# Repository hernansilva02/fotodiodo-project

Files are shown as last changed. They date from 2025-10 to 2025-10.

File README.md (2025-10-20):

# Fotodiodo Project — Detector con fotodiodo + TIA

Proyecto académico/open-hardware para el diseño, simulación y fabricación de un detector basado en **fotodiodo PIN** con **amplificador transimpedancia (TIA)**. El repositorio incluye esquemáticos y PCB en KiCad, modelos/SPICE para simulación, gerbers listos para fabricación y documentación en LaTeX.

> Licencia: **CERN Open Hardware License v1.2** (incluida en el repo).

---

## ✨ Características

- **Hardware KiCad**: esquemáticos y PCB en `KiCAD/` con vistas 2D/3D y archivos de fabricación en `gerbers/`.
- **Simulación**: netlists y archivos en `spice/` para análisis de ruido, frecuencia y transitorios del TIA.
- **Documentación**: fuentes LaTeX en `docs/` (compilables con `latexmk` o `pdflatex + bibtex`).
- **Datasheets** de componentes relevantes en `datasheets/`.
- **Licencia**: archivo `CERN_OPEN_HARDWARE_LICENSE_OHL_v_1_2.txt` en la raíz.

---

## 🔧 Requisitos

- **KiCad** (>= 6.x recomendado) para abrir `KiCAD/`.
- **Simulador SPICE** (LTspice/Ngspice) para `spice/`.
- **LaTeX** para compilar `docs/` (p. ej. `latexmk` o `pdflatex + bibtex`).

---

## ▶️ Cómo usar

### 1) Hardware (KiCad)
1. Abrí el proyecto desde `KiCAD/`.
2. Revisá el esquemático y el stackup; validá DRC/ERC.
3. Para visualizar en 3D, usá el visor de KiCad.
4. Si necesitás fabricar, exportá desde el proyecto o usá los **archivos listos** en `gerbers/`.

### 2) Simulación (SPICE)
1. Abrí los archivos de `spice/` con tu simulador.
2. Corré análisis **AC** (ganancia/banda), **TRAN** (respuesta a pulsos) y **ruido**.
3. Ajustá la **Rf** del TIA y **Cf** de compensación según tu fotodiodo/carga esperada.

### 3) Documentación (LaTeX)
- Compilación rápida:
  ```bash
  cd docs
  latexmk -pdf
  # o, alternativamente
  pdflatex main.tex && bibtex main && pdflatex main.tex && pdflatex main.tex

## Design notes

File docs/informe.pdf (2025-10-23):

# Detector de Part´ıculas Beta

Hernan Alejandro Silva ´
Facultad Regional Avellaneda Universidad Tecnologica Nacional ´ Buenos Aires, Argentina
hernansilva2002@gmail.com

El´ıas Ram´ırez
Facultad Regional Avellaneda Universidad Tecnologica Nacional ´ Buenos Aires, Argentina
ramirezelias.marcos@gmail.com

Florencia Mincone
Facultad Regional Avellaneda Universidad Tecnologica Nacional ´ Buenos Aires, Argentina
flormincone1@gmail.com

Nicolas Lahorca ´
Facultad Regional Avellaneda Universidad Tecnologica Nacional ´ Buenos Aires, Argentina
nicolas.lahorca.k@gmail.com

Luciano Justiniano
Facultad Regional Avellaneda Universidad Tecnologica Nacional ´ Buenos Aires, Argentina
luciano.nicolas.justiniano@gmail.com

Abstract—Constantemente los objetos que nos rodean emiten part´ıculas que los sentidos humanos no son capaces de percibir. Estas part´ıculas pueden ser perjudiciales para la salud y es necesario cuantificarlas y/o detectarlas para evitar o reducir la exposicion a ellas. Para lograr ese objetivo, en este documento se ´
presenta la realizacion de un dispositivo que cumpla la funci ´ | on de ´
detectar un tipo de radiacion, llamada radiaci ´ | on´ β. En particular,
se hara hincapi ´ | e en la radiaci ´ | on por emisi ´ | on de electrones, a este ´
tipo de radiacion se la conoce como radiaci ´ | on´ | β−. Ademas, ´
se propone el analisis de su principio de funcionamiento, los ´ materiales necesarios para su construccion y sus limitaciones. ´
I. INTRODUCCION´
El presente documento sirve como informe sobre el proyecto
de fin de ano de la asignatura F ˜ | | | ´ısica Electronica. Dicho ´
proyecto se trata de un detector y contador de part´ıculas beta, cubriendo de esta forma el tema radiacion de la asignatura. ´
Para mas informaci ´ | on sobre el proyecto, se recomienda visitar ´
el repositorio del mismo [1].

II. PRINCIPIO DE FUNCIONAMIENTO
A. ¿Que son las radiaciones β?
Las radiaciones β son un tipo de radiacion ionizante, la cual ´ se caracteriza por emitirse durante el proceso de desintegracion´ o decaimento β. Dicho proceso puede producirse de dos diferentes formas.
1) Emision de electrones ´ | : Un nucleo inestable de un ´ | atomo ´
emite un electron y un antineutrino, conviritiendo de esta ´
manera un neutron en un prot ´ | on como ´ | Desintegracion´
β−.
2) Emision de positrones ´ | : El nucleo inestable emite un ´
positron, es decir, la antipart ´ | | | ´ıcula del electron, junto ´
con un neutrino. De esta forma se logra transformar un
proton en un neutr ´ | on. Este proceso recibe el nombre de ´
Desintegracion´ β+.
Generalmente, las fuentes mas comunes de radiaci ´ | on de ´
part´ıculas β son piedras con pequenas cantidades de uranio, ˜ y diferentes fuentes de potasio, como el cloruro de potasio
(KCl), el cual contiene baja cantidad del is ´ | otopo potasio 40 ´
(K40), capaz de emitir part ´ | | ´ıculas β−.
B. Formas de captar las part´ıculas
El dispositivo electronico m ´ | as estudiado y utilizado para ´
detectar la radiacion de diferentes tipos de part ´ | ´ıculas es el
diodo PIN o fotodiodo. Como muestra la Fig. 1, este es similar en cuanto a estructura a un diodo de juntura PN, la diferencia radica en que el PIN tiene una zona de material semiconductor intr´ınseco (zona I) entre la zona dopada positivamente (zona
P) y la zona dopada negativamente (zona N).
Al ser un material semiconductor, la zona I contiene atomos ´ de silicio que, al momento de ser impactados por una part´ıcula irradiada debido a una fuente radioactiva, genera la rotura de
los enlaces covalentes del atomo, produciendo un ´ | par electron- ´
laguna. La generacion de este par tiene como consecuencia un ´ pulso de corriente de decenas hasta cientos de microampere que atraviesan al diodo. Esta corriente puede ser medida. Cuando al diodo se lo polariza en forma inversa (catodo con ´
potencial mas alto que el del ´ | anodo), se generan dos regiones ´
de vaciamiento: La primera se encuentra localizada entre la zona P y la zona I, y la otra entre dicha zona intr´ınseca y la zona N; en estas regiones, no se encuentran portadores libres, sino que exisen iones fijos cargados positiva y negativamente. Estos iones fijos son los responsables que en dichas regiones
se encuentre un campo electrico, el c ´ | ual atrapa e impulsa a los ´
portadores, aumentando la intensidad de corriente electrica a ´ traves del diodo. ´
Anodo (A) ´ | Catodo (K) ´

P

+ | I | N +

Wi

Fig. 1. Corte transversal de una estructura t´ıpica del diodo PIN

C. El fotodiodo como detector de part´ıculas β

La zona intr´ınseca explicada anteriormente es conocida como zona sensible, porque es donde las part´ıculas irradiadas impactan. Como se menciona en [2], las zonas sensibles de los fotodiodos son capaces de absorber algunos tipos de radia-
ciones ionizantes. La deteccion de las part ´ | ´ıculas que impactan
esta directamente relacionada con la profundidad de la zona ´ sensible del diodo; esta zona (region de vaciamiento) aumenta ´ de profundidad al elevar el voltaje de polarizacion inversa del ´
dispositivo, dicha relacion responde matem ´ | aticamente a ´

d(V ) = εrε0A
C(V )
| (1)

donde:
- d(V) es la profunidad de la zona sensible.
- εr es la permitividad relativa del material, en este caso el Si (silicio).
- ε0 es la permitividad del vac´ıo.
- A es el area f ´ ´ısica de la zona sensible del diodo.
- C(V) es la capacitancia del diodo a un determinado nivel de voltaje de polarizacion inversa. ´
Este valor de profundidad permite conocer la energ´ıa
cinetica m ´ | axima que se puede detectar de una part ´ | ´ıcula. Como
se menciono anteriormente, los valores de inter ´ | es correspon- ´
den a part´ıculas β− (electrones). Para establecer el valor de energ´ıa mencionado, es necesario conocer la magnitud del rango CSDA (continuos slowing down approximation). El rango CSDA es una aproximacion muy cercana de la media de ´ longitud de una trayectoria que recorre una part´ıcula cargada a medida que se frena hasta alcanzar el reposo [3]. Para los electrones, los valores del CSDA estan tabulados en [3]. ´ Para obtener una medicion fiable, es necesario que el rango ´ CSDA sea menor o igual que la profundidad de la zona sensible del diodo; esto es
Rp ≤ d(V ) | (2)

donde Rp es el rango CSDA.
De esta forma, la energ´ıa de la part´ıcula incidente es completamente disipada en el interior de la zona sensible.

III. CARACTER´ISTICAS CONTRUCTIVAS DEL DETECTOR

El dispositivo a realizar para detectar las part´ıculas tiene
como foco ser portable y producir una senal de detecci ˜ | on a la ´
salida con amplitud observable al medir con un osciloscopio digital. Con estos objetivos definidos, el dispositivo estara´ compuesto por dos etapas:
- Etapa de deteccion: La opci ´ | on mas documentada para la ´
deteccion de estas part ´ | ´ıculas es el diodo PIN BPW34, que
es posible observar en la Fig. 2(a); si se logra aislarlo completamente de la luz incidente y de interferencias electromagneticas, es capaz de detectar radiaciones ion- ´ izantes en su zona sensible.

Para aumentar la superficie total de deteccion, el circuito ´ utiliza 4 diodos en paralelo. Esto no modifica el valor de profundidad de la zona sensible calculada a partir de (1).
- Etapa de amplificacion: Es necesario tener un nivel de ´ ruido muy reducido, ya que un nivel alto esconder´ıa los picos debido a los impactos de las part´ıculas. El candidato ideal que satisface esos requerimientos es un amplificador operacional de alta impedancia de entrada, como lo es la serie OPAx134 del fabricante Texas Instruments. A su vez, esta etapa esta compuesta por una etapa de tran- ´ simpedancia (conversion de la corriente de los fotodiodos ´
en tension) y otra de amplificaci ´ | on diferencial. ´
Ambas etapas deben tener su especificacion correspondi- ´ ente.
A. Etapa de deteccion´

Debido a que uno de los objetivos es que el dispositivo detector sea portable, la alimentacion del circuito es de una ´ bater´ıa de 9 V, con una tension nominal de 9,9 V. Con ´ este valor de alimentacion, el circuito amplificador entrega ´ aproximadamente 8 V de polarizacion inversa a los diodos. ´ La Fig. 2(b) muestra que para un nivel de tension de 8 V de ´ VR corresponde una capacitancia de aproximadamente 22 pF. Reemplazando la capacitancia (para 8 V de VR) en (1), se obtiene

d(V ) = 11, 68 × 8, 85 × 10⁻¹² F · m⁻¹ × 7.02 mm² 22 pF
d(V ) = 32, 98 µm
d(V ) ≈ 33 µm
Esto nos indica que un electron puede viajar como m ´ | aximo ´
33 µm dentro de la zona sensible, de manera tal que se cumpla lo expresado con anterioridad en (2).
Debido a que la base de datos de [3] expresa los valores de rango CSDA en unidades de g/cm²
, es necesario que el d(V) calculado este tambi ´ en en dicha unidad; para esto, calculamos ´

σ = ρ t

donde σ es la densidad superficial, ρ es la densidad del silicio y t es el espesor de la zona sensible (d(V) calculado).
Para 33 µm, esto es

σ = ρ t
σ = 2, 32 g · cm⁻³ × 0, 0033 cm = 7, 6 × 10⁻³

g · cm⁻²

En la base de datos de [3] es posible observar que para el
Si, la energ´ıa cinetica m ´ | axima del electr ´ | on para un rango de ´
7, 6 × 10⁻³ g · cm⁻² | es 60 KeV.
Con el fin de anular interferencias electromagneticas exter- ´ nas y la luz del ambiente, el circuito se ubica dentro de un gabinete estanco de aluminio.

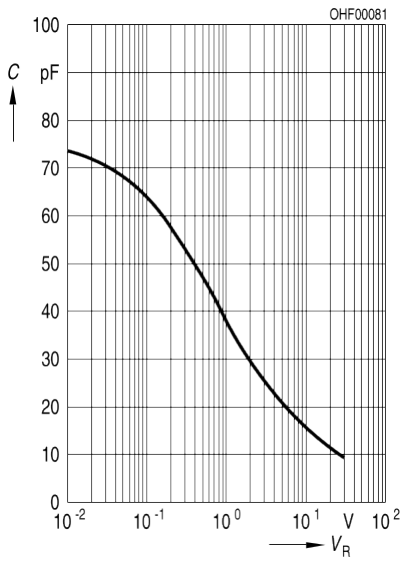
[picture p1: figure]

(a) (b)

Fig. 2. Fotodiodo BPW34S de la marca Osram. (a) Imagen real del fotodiodo. ´
(b) Curva caracter´ıstica C-V del BPW34S
B. Etapa de amplificacion´
El amplificador operacional, cuyas descripciones se explico´ anteriormente, consta de 2 etapas; ambas se pueden ver en la Fig. 3.
- Etapa de transimpedancia (primer etapa): Para transformar los picos de corriente en picos de voltaje es necesario utilizar un primer amplificador en configuracion´ transimpedancia; su caracter´ıstica fundamental es que la corriente generada en los diodos (decenas de microampere) atraviesa una resistencia de realimentacion de valor ´ grande, generando, por ley de Ohm, una caida de tension´ en ella. A la salida del primer amplificador tendremos

Vout1 = Vref1 − ID Rf b

donde Vref1 = V R1/(R1 + R2) es la tension de ´ referencia del primer amplificador; su valor tiene que ser 8 V y se logra a partir del divisor de voltaje entre las resistencias R1 y R2 de la Fig. 3. ID es la corriente de los diodos y Rfb es la resistencia de realimentacion´ (feedback), equivalente a R3 en la Fig. 3
- Etapa de amplificacion (segunda etapa): ´ | | | Vout1 es de valor
de tension muy d ´ | ebil, por ello es necesario amplificar la ´
salida de la primer etapa. Esto es posible mediante un segundo amplificador que toma como entrada Vout1. Al utilizar 2 amplificadores operacionales (uno por etapa), es necesario adoptar el amplificador OPA2134 de la l´ınea OPAx134 previamente mencionada.

IV. LIMITACIONES DEL DISENO˜

Las limitaciones o posibles mejoras del diseno actual son ˜ las siguientes
1) Niveles de energ´ıa cinetica detectables: Como se ha ´
expresado anteriormente, el nivel maximo de energ ´ | ´ıa
medible es 60 KeV, lo cual es un valor relativamente bajo ´
para part´ıculas β−; part´ıculas con mas energ ´ | ´ıa no seran´
medidas correctamente. Esto es debido principalmente al
area efectiva de detecci ´ | on ( ´ | area f ´ | ´ısica de la zona sensible
de los diodos) y al valor de capacitancia del diodo para

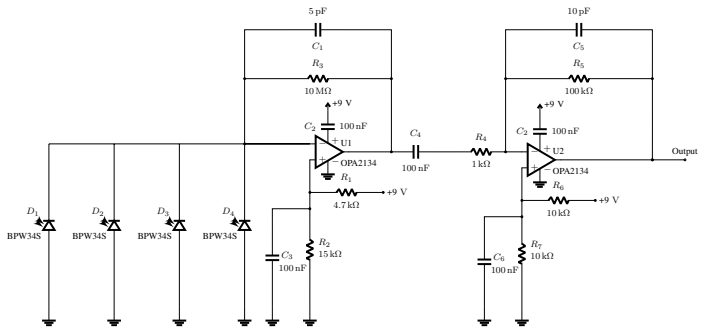
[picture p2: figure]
BPW34S; −OPA2134; OPA2134; Output

Fig. 3. Circuito completo

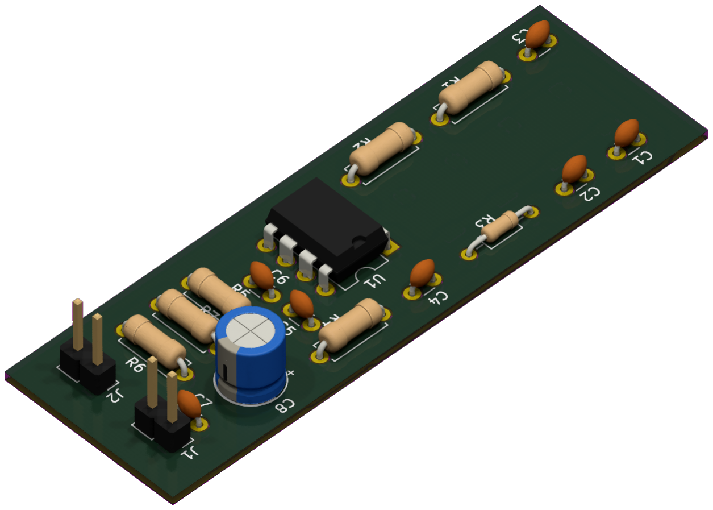
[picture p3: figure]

(a)

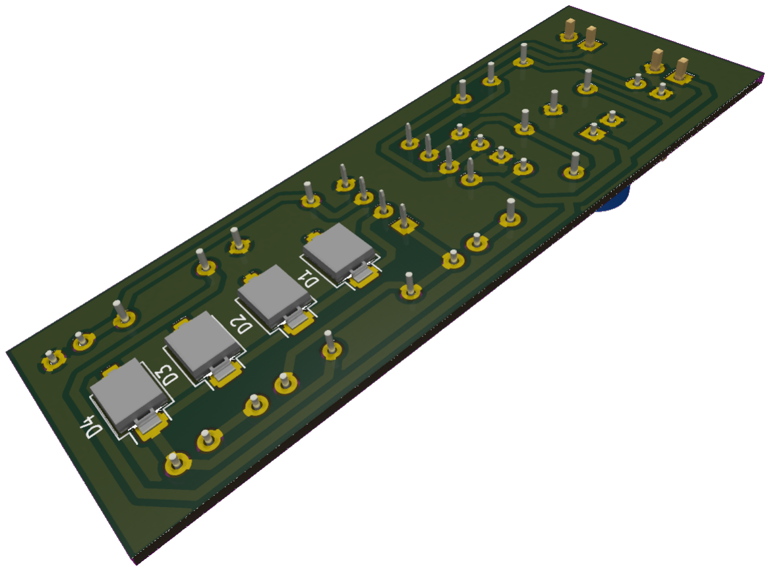
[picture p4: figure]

(b)

Fig. 4. Modelado 3D del PCB. (a) Parte frontal, (b) parte posterior

VR dado. Una mejora viable para este problema es el aumento del voltaje de alimentacion, de manera tal que ´ aumente VR.
2) Nivel de ruido: el capacitor C4 que se puede observar en la Fig. 3 tiene un papel fundamental en los niveles de ruido de la salida del circuito. Emp´ıricamente se pudo advertir que utilizando un valor de 22 pF en lugar de 5 pF, las mediciones de los picos fueron mas limpias. ´
V. CONCLUSIONES
Aunque el diseno de detectores de part ˜ | ´ıculas con fotodiodos
requiere de un nivel de precision muy grande para evitar ca- ´ pacitancias parasitas y obtener el menor nivel de ruido posible ´ montado en la senal de salida, es posible realizar mediciones ˜ de radiacion´ β− utilizando un amplificador operacional basado en JFET en configuracion transimpedancia. ´

REFERENCES

[1] H. Silva, “Detector de part´ıculas beta,” [Accedido: 23 Oct. 2025]. [Online]. Available: https://github.com/hernansilva02/fotodiodo-project. git
[2] O. Keller, M. Benoit, A. Muller, and S. Schmeling, “Smartphone and ¨ tablet-based sensing of environmental radioactivity: Mobile low-cost measurements for monitoring, citizen science, and educational purposes,” Sensors, vol. 19, 2019. [Online]. Available: https://www.mdpi.com/1424-8220/19/19/4264

[3] M. Berger, J. Coursey, M. Zucker, and J. Chang, “Stopping-
power | & | range | tables | for | electrons, | protons, | and | helium
ions,” National Institute of Standards and Technology, Tech. Rep., October 2009. [Online]. Available: https://www.nist.gov/pml/stopping-power-range-tables-electrons-protons-and-helium-ions
[4] U.S Department of Energy. Doe explains...beta decay. [Online]. Available: https://www.energy.gov/science/doe-explainsbeta-decay
[5] Ozel, “Diy particle detector,” [Accedido: 23 Oct. 2025]. [Online]. Available: https://github.com/ozel/DIY particle detector.git

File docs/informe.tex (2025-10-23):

\documentclass[a4paper,conference]{IEEEtran}
\usepackage{graphicx}
\usepackage{amsmath}
\usepackage{url}
\usepackage[RPvoltages]{circuitikz}
\usepackage{tikz}
\usepackage{siunitx}
\ifCLASSOPTIONcompsoc
    \usepackage[caption=false,font=normalsize,labelfont=sf,textfont=sf]{subfig}
\else
    \usepackage[caption=false,font=footnotesize]{subfig}
\fi

\makeatletter
\newcommand{\authornewline}{
        \end{@IEEEauthorhalign}
        \hfill\mbox{}\par\mbox{}\hfill
        \begin{@IEEEauthorhalign}
}
\makeatother

\author{
    \IEEEauthorblockN{Hernán Alejandro Silva}
    \IEEEauthorblockA{
        Facultad Regional Avellaneda\\
        Universidad Tecnológica Nacional\\
        Buenos Aires, Argentina\\
        hernansilva2002@gmail.com
    }
    \and
    \IEEEauthorblockN{Elías Ramírez}
    \IEEEauthorblockA{
        Facultad Regional Avellaneda\\
        Universidad Tecnológica Nacional\\
        Buenos Aires, Argentina\\
        ramirezelias.marcos@gmail.com
    }
    \and
    \IEEEauthorblockN{Florencia Mincone}
    \IEEEauthorblockA{
        Facultad Regional Avellaneda\\
        Universidad Tecnológica Nacional\\
        Buenos Aires, Argentina\\
        flormincone1@gmail.com
    }
    \authornewline
    \IEEEauthorblockN{Nicolás Lahorca}
    \IEEEauthorblockA{
        Facultad Regional Avellaneda\\
        Universidad Tecnológica Nacional\\
        Buenos Aires, Argentina\\
        nicolas.lahorca.k@gmail.com
    }
    \and
    \IEEEauthorblockN{Luciano Justiniano}
    \IEEEauthorblockA{
        Facultad Regional Avellaneda\\
        Universidad Tecnológica Nacional\\
        Buenos Aires, Argentina\\
        luciano.nicolas.justiniano@gmail.com
    }
}
\title{Detector de Partículas Beta}

\begin{document}
\maketitle
\begin{abstract}
    Constantemente los objetos que nos rodean emiten partículas que los sentidos
    humanos no son capaces de percibir. Estas partículas pueden ser
    perjudiciales para la salud y es necesario cuantificarlas y/o detectarlas
    para evitar o reducir la exposición a ellas. Para lograr ese objetivo, en
    este documento se presenta la realización de un dispositivo que cumpla la
    función de detectar un tipo de radiación, llamada radiación
    $\boldsymbol{\beta}$. En particular, se hará hincapié en la radiación por
    emisión de electrones, a este tipo de radiación se la conoce como radiación
    $\boldsymbol{\beta-}$. Además, se propone el análisis de su principio de
    funcionamiento, los materiales necesarios para su construcción y sus
    limitaciones.
\end{abstract}
\section{Introducción}
    El presente documento sirve como informe sobre el proyecto de fin de año de
    la asignatura Física Electrónica. Dicho proyecto se trata de un detector y
    contador de partículas beta, cubriendo de esta forma el tema radiación de
    la asignatura. Para más información sobre el proyecto, se recomienda
    visitar el repositorio del mismo \cite{git_repo}.
\section{Principio de Funcionamiento}
    \subsection{¿Que son las radiaciones $\beta$?}
        Las radiaciones $\beta$ son un tipo de radiacion ionizante, la cúal se
        caracteriza por emitirse durante el proceso de desintegración o
        decaimento $\beta$. Dicho proceso puede producirse de dos diferentes
        formas.
        \begin{enumerate} 
            \item \textit{Emisión de electrones}: Un núcleo inestable de un
                átomo emite un electrón y un antineutrino, conviritiendo de esta
                manera un neutrón en un protón como \emph{Desintegración $\beta-$}.
            \item \textit{Emisión de positrones}: El núcleo inestable emite un
                positrón, es decir, la antipartícula del electrón, junto con
                un neutrino. De esta forma se logra transformar un protón en un
                neutrón. Este proceso recibe el nombre de
                \emph{Desintegración $\beta+$}. 
        \end{enumerate}

        Generalmente, las fuentes más comunes de radiación de partículas $\beta$
        son piedras con pequeñas cantidades de uranio, y diferentes fuentes de
        potasio, como el cloruro de potasio (KCl), el cúal contiene baja
        cantidad del isótopo potasio 40 (K40), capáz de emitir partículas
        $\beta-$.

    \subsection{Formas de captar las partículas}
       El dispositivo electrónico más estudiado y utilizado para detectar la
       radiación de diferentes tipos de partículas es el diodo PIN o fotodiodo.
       Como muestra la Fig.~\ref{fig:pin}, este es similar en cuanto a
       estructura a un diodo de juntura PN, la diferencia radica en que el PIN
       tiene una zona de material semiconductor intrínseco (zona I) entre la
       zona dopada positivamente (zona P) y la zona dopada negativamente (zona
       N).\par Al ser un material semiconductor, la zona I contiene átomos de
       silicio que, al momento de ser impactados por una partícula irradiada
       debido a una fuente radioactiva, genera la rotura de los enlaces
       covalentes del átomo, produciendo un \emph{par electrón-laguna}. La
       generación de este par tiene como consecuencia un pulso de corriente de
       decenas hasta cientos de microampere que atraviesan al diodo. Esta
       corriente puede ser medida. Cuando al diodo se lo polariza en
       forma inversa (cátodo con potencial más alto que el del ánodo),
       se generan dos regiones de vaciamiento: La primera se encuentra
       localizada entre la zona P y la zona I, y la otra entre dicha zona
       intrínseca y la zona N; en estas regiones, no se encuentran portadores
       libres, sino que exisen iones fijos cargados positiva y negativamente.
       Estos iones fijos son los responsables que en dichas regiones se encuentre
       un campo eléctrico, el cúal atrapa e impulsa a los portadores, aumentando
       la intensidad de corriente eléctrica a través del diodo.
       \begin{figure}[!b]
           \centering
           \begin{tikzpicture}[line cap=round,line join=round,scale=0.8]
  % Dimensiones base
               \def\Hsd{1.6} % altura del semiconductor
               \def\W{8.0} % ancho total
               \def\xP{2.0} % fin de P
               \def\xI{5.0} % fin de I (inicio de N)

  % Contorno del semiconductor
               \draw[very thick] (0,0) rectangle (\W,\Hsd);

  % Rellenos (en escala de grises apta IEEE)
               \fill[gray!25]    (0,0) rectangle (\xP,\Hsd);          % P+
               \fill[gray!5]     (\xP,0) rectangle (\xI,\Hsd);         % I
               \fill[gray!35]    (\xI,0) rectangle (\W,\Hsd);          % N+

               \draw[dashed,gray!60] (\xP,0) -- (\xP,\Hsd);
               \draw[dashed,gray!60] (\xI,0) -- (\xI,\Hsd);

  % Contactos metálicos (superiores) y terminales
  % P+: metal
               \fill[black!60] (0.3,\Hsd) rectangle (1.7,\Hsd+0.3);
               \draw[very thick] (1.0,\Hsd+0.3) -- (1.0,\Hsd+1.0) node[above]{\small Ánodo (A)};
  % N+: metal
               \fill[black!60] (6.3,\Hsd) rectangle (7.7,\Hsd+0.3);
               \draw[very thick] (7.0,\Hsd+0.3) -- (7.0,\Hsd+1.0) node[above]{\small Cátodo (K)};

  % Etiquetas de regiones
           \node at ({1.0},{0.5*\Hsd}) {\large P$^{\boldsymbol{+}}$};
               \node at ({0.5*(\xP+\xI)},{0.5*\Hsd}) {\large I};
           \node at ({0.5*(\xI+\W)},{0.5*\Hsd}) {\large N$^{\boldsymbol{+}}$};

  % Ancho de la región intrínseca (Wi)
               \draw[|-|] (\xP,-0.35) -- (\xI,-0.35)
               node[midway,below=2pt] {$W_i$};
           \end{tikzpicture}
           \caption{Corte transversal de una estructura típica del diodo PIN}
           \label{fig:pin}
       \end{figure}
    \subsection{El fotodiodo como detector de partículas $\beta$}
        La zona intrínseca explicada anteriormente es conocida como \emph{zona
        sensible}, porque es donde las partículas irradiadas impactan. Como se
        menciona en \cite{mpdi}, las zonas sensibles de los fotodiodos son
        capaces de absorber algunos tipos de radiaciones ionizantes. La
        detección de las partículas que impactan está directamente relacionada
        con la profundidad de la zona sensible del diodo; esta zona (región de
        vaciamiento) aumenta de profundidad al elevar el voltaje de polarización
        inversa del dispositivo, dicha relación responde matemáticamente a

        \begin{equation}
            \label{d_x}
            d(V) = \frac{\varepsilon_{r}\varepsilon_{0}A}{C(V)}
        \end{equation}

        \hfill \\ donde:
        \begin{itemize}
            \item d(V) es la profunidad de la zona sensible.
            \item $\varepsilon_{r}$ es la permitividad relativa del material, en este caso el Si
                (silicio).
            \item $\varepsilon_{0}$ es la permitividad del vacío.
            \item A es el área física de la zona sensible del diodo.
            \item C(V) es la capacitancia del diodo a un determinado nivel de
                voltaje de polarización inversa.
        \end{itemize}

        Este valor de profundidad permite conocer la energía cinética máxima que
        se puede detectar de una partícula. Como se mencionó anteriormente, los
        valores de interés corresponden a partículas $\beta-$ (electrones). Para
        establecer el valor de energía mencionado, es necesario conocer la
        magnitud del rango \emph{CSDA (continuos slowing down approximation)}.
        El rango CSDA es una aproximación muy cercana de la media de longitud de
        una trayectoria que recorre una partícula cargada a medida que se frena
        hasta alcanzar el reposo \cite{nist}. Para los electrones, los valores
        del CSDA están tabulados en \cite{nist}.\par 
        Para obtener una medición fiable, es necesario que el rango CSDA sea
        menor o igual que la profundidad de la zona sensible del diodo; esto es
        \begin{equation}
            R_{p} \leq d(V)
            \label{eq:range}
        \end{equation}

        \hfill \\ donde $\mathrm{R_{p}}$ es el rango CSDA.\\
        De esta forma, la energía de la partícula incidente es completamente
        disipada en el interior de la zona sensible.

    \section{Características Contructivas del Detector}
        El dispositivo a realizar para detectar las partículas tiene como foco
        ser portable y producir una señal de detección a la salida con amplitud
        observable al medir con un osciloscopio digital. Con estos objetivos
        definidos, el dispositivo estará compuesto por dos etapas:
        \begin{itemize}
            \item Etapa de detección: La opción mas documentada para la
                detección de estas partículas es el diodo PIN BPW34, que es
                posible observar en la Fig.~\ref{fig:bpw34}\subref{subfig:bpw34}; si se logra
                aislarlo completamente de la luz incidente y de interferencias
                electromagnéticas, es capaz de detectar radiaciones ionizantes
                en su zona sensible.\par
                Para aumentar la superficie total de detección, el circuito
                utiliza 4 diodos en paralelo. Esto no modifica el valor de
                profundidad de la zona sensible calculada a partir de
                (\ref{d_x}).
            \item Etapa de amplificación: Es necesario tener un nivel de ruido
                muy reducido, ya que un nivel alto escondería los picos debido a
                los impactos de las partículas. El candidato ideal que satisface
                esos requerimientos es un amplificador operacional de alta
                impedancia de entrada, como lo es la serie OPAx134 del
                fabricante Texas Instruments. A su vez, esta etapa está
                compuesta por una etapa de transimpedancia (conversión de la
                corriente de los fotodiodos en tensión) y otra de amplificación
                diferencial.
        \end{itemize}

        Ambas etapas deben tener su especificación correspondiente.

        \subsection{Etapa de detección}
            Debido a que uno de los objetivos es que el dispositivo detector sea
            portable, la alimentación del circuito es de una batería de 9 V, con
            una tensión nominal de 9,9 V. Con este valor de alimentación, el
            circuito amplificador entrega aproximadamente 8 V de polarización
            inversa a los diodos. La Fig.~\ref{fig:bpw34}\subref{subfig:c-v}
            muestra que para un nivel de tensión de 8 V de $\mathrm{V_{R}}$
            corresponde una capacitancia de aproximadamente 22 pF.\par
            Reemplazando la capacitancia (para 8 V de $\mathrm{V_{R}}$) en
            (\ref{d_x}), se obtiene

            \begin{IEEEeqnarray*}{rCl}
                d(V) & = & \frac{11,68\times 8,85\times10^{-12}\ \mathrm{F}\cdot
                \mathrm{m^{-1}}\times 7.02\ \mathrm{mm^{2}}} {22\ \mathrm{pF}} \\
                    d(V) & = & 32,98\ \mathrm{\mu m}   \\
                    d(V) & \approx & 33\ \mathrm{\mu m} 
            \end{IEEEeqnarray*}

            Esto nos indica que un electrón puede viajar como máximo 33
            $\mathrm{\mu m}$ dentro de la zona sensible, de manera tal que se
            cumpla lo expresado con anterioridad en (\ref{eq:range}).\par
            Debido a que la base de datos de \cite{nist} expresa los valores de
            rango CSDA en unidades de $\mathrm{g/cm^{2}}$, es necesario que el d(V)
            calculado esté también en dicha unidad; para esto, calculamos
            \begin{equation*}
                \sigma = \rho~t
            \end{equation*}
            donde $\sigma$ es la densidad superficial, $\rho$ es la densidad del
            silicio y t es el espesor de la zona sensible (d(V) calculado).

            \begin{figure}[ht]
                \centering
                \subfloat[] {%
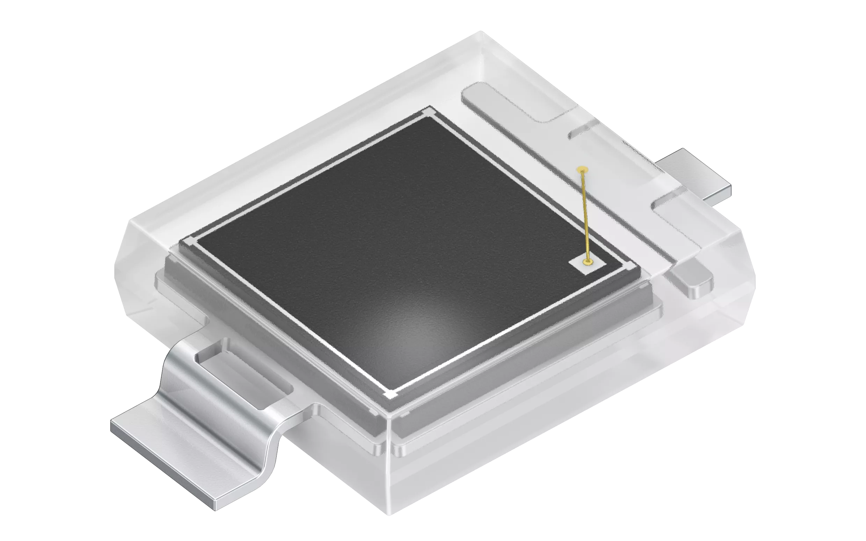
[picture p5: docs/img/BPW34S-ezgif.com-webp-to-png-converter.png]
                    
                    \label{subfig:bpw34}
                }
                \hfil
                \subfloat[] {%
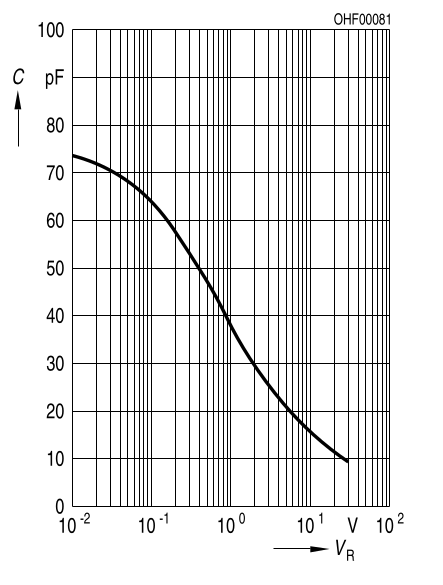
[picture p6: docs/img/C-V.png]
                    
                    \label{subfig:c-v}
                }
                \caption{Fotodiodo BPW34S de la marca Osram. (a) Imágen real del
                fotodiodo. (b) Curva característica C-V del BPW34S}
                \label{fig:bpw34}
            \end{figure}

            Para 33 $\mathrm{\mu m}$, esto es
            \begin{IEEEeqnarray*}{C} %deberia usar \begin{equation} con \begin{split}
                \sigma=\rho~t\\
                \sigma= 2,32\ \mathrm{g\cdot cm^{-3}}\ \times \ 0,0033\
                \mathrm{cm}\\%
                       = 7,6\times 10^{-3}\ \mathrm{g\cdot cm^{-2}}
            \end{IEEEeqnarray*}

            En la base de datos de \cite{nist} es posible observar que para el
            Si, la energía cinética máxima del electrón para un rango de
            $7,6\times 10^{-3}\ \mathrm{g\cdot cm^{-2}}$ es 60 KeV.

            Con el fin de anular interferencias electromagnéticas externas y la
            luz del ambiente, el circuito se ubica dentro de un gabinete
            estanco de aluminio.
        \subsection{Etapa de amplificación}
            El amplificador operacional, cuyas descripciones se explicó
            anteriormente, consta de 2 etapas; ambas se pueden ver en la
            Fig.~\ref{fig:circ}.
            \begin{itemize}
                \item Etapa de transimpedancia (primer etapa): Para transformar
                    los picos de corriente en picos de voltaje es necesario
                    utilizar un primer amplificador en configuración
                    transimpedancia; su característica fundamental es que la
                    corriente generada en los diodos (decenas de microampere)
                    atraviesa una resistencia de realimentación de valor grande,
                    generando, por ley de Ohm, una caida de tensión en ella. A
                    la salida del primer amplificador tendremos
                    \begin{equation*}
                        V_{out1} = V_{ref1} - I_{D}\ R_{fb}
                    \end{equation*}
                    donde $\mathrm{V_{ref1}} = V\ R1/(R1+R2)$ es la tensión de referencia del
                    primer amplificador; su valor tiene que ser 8 V y se logra a
                    partir del divisor de voltaje entre las resistencias R1 y R2
                    de la Fig.~\ref{fig:circ}. $\mathrm{I_{D}}$ es la corriente
                    de los diodos y $\mathrm{R_{fb}}$ es la resistencia de
                    realimentación (\emph{feedback}), equivalente a R3 en
                    la Fig.~\ref{fig:circ}
                \item Etapa de amplificación (segunda etapa):
                    $\mathrm{V_{out1}}$ es de valor de tensión muy débil, por
                    ello es necesario amplificar la salida de la primer etapa.
                    Esto es posible mediante un segundo amplificador que toma
                    como entrada $\mathrm{V_{out1}}$.
            \end{itemize}

            Al utilizar 2 amplificadores operacionales (uno por etapa), es
            necesario adoptar el amplificador OPA2134 de la línea OPAx134
            previamente mencionada. 
            \tikzset{every picture/.style={/tikz/font=\normalsize}}

            \begin{figure}[!t]
                \centering
                \ctikzset{bipoles/length=7mm, amp symbol font={\footnotesize}}
                \begin{circuitikz}[american, font=\footnotesize, transform shape,
                    scale=0.46]
    %\ctikzset{diodes/scale=0.5}
                    \centering
                    \draw
                    (0,0) to[photodiode,name=D1] (0,5)
                    node[above left=5pt](D1label) at (D1) {$D_{1}$}
                    node[below left=3pt] at (D1) {BPW34S}
                    (0,0) node[ground, scale=2] {}

                    (2,0) to[photodiode,name=D2] (2,5)
                    node[above left=5pt] at (D2) {$D_{2}$}
                    node[below left=3pt] at (D2) {BPW34S}
                    (2,0) node[ground, scale=2] {}

                    (4,0) to[photodiode,name=D3] (4,5)
                    node[above left=5pt] at (D3) {$D_{3}$}
                    node[below left=3pt] at (D3) {BPW34S}
                    (4,0) node[ground, scale=2] {}

                    (6,0) to[photodiode,name=D4] (6,5) coordinate(vd4)
                    node[above left=5pt] at (D4) {$D_{4}$}
                    node[below left=3pt] at (D4) {BPW34S}
                    (6,0) node[ground, scale=2](d4gnd) {}

    % muevo el cursor desde gnd de D4 hasta donde termina la pata de D4 creo una linea desde el D4 con long = 1
                    ++(0,5)
                    to[short] ++(2,0)

                    node[op amp, anchor=-] (opamp) {}
                    (0,5) -- (opamp.-)
                    (opamp.up) ++ (.2,0) node[right=2pt] {U1}
                    (opamp.down) ++ (.2,0) node[below=2pt, right=2pt] {OPA2134}
                    (opamp.down) -- node[ground, scale=2] {} ++(0,0)
                    (opamp.down) node[below=1pt, right] {$-$}
                    (opamp.up) node[above=2pt, right=-0.5pt] {$+$}
                    (opamp.+) -- ++(0,-1) coordinate(VD1)
    % primer divisor
                    to[R] node[above=35pt, right=4pt] {$R_{2}$} node[above=25pt,
                    right=4pt] {\SI{15}{\kilo\ohm}} (VD1 |- d4gnd) node[ground, scale=2] {}
                    (VD1) to[short,*-] ++(.75,0)
                    to[R, l=$R_{1}$, a=\SI{4.7}{\kilo\ohm}] ++(.75,0) to[short,-*] ++(.75,0) node[right] {+9 $\mathrm{V}$} % Resistencia del divisor
                    (VD1) ++(0,-.5) to[short, *-] ++(-1.15,0) coordinate(cR2)
                    to[C] node[above=5.5ex, right=1ex] {$C_{3}$} node[above=3ex, right=.5ex] {\SI{100}{\nano\farad}} (cR2 |- d4gnd) node[ground, scale=2] {}
                    (opamp.up) %-- ++(0,.5) coordinate(V+C1)
                    to[C, l=$C_{2}$, a=\SI{100}{\nano\farad}] ++(0,1) node[vcc](vcc) {} node[above right=.5pt] {+9~V}
                    (vd4) to[short, *-] ++(0,2)
                    to[R, l=$R_{3}$, a=\SI{10}{\mega\ohm}] ++(4.5,0) coordinate(r3_out1)
                    (opamp.out) -- (r3_out1 |- opamp.out) coordinate(vout1_node1)
    % capacitor en paralelo a R3
    %(r3_out1) to[short, *-] ++(0,1)
                    to[short,*-] (vout1_node1 |- r3_out1)
                    (vout1_node1 |- vout1_node1) to[C, l=$C_{4}$,
                    a=\SI{100}{\nano\farad}] ++(1.5,0)
                    to[R, l=$R_{4}$, a=\SI{1}{\kilo\ohm}] ++(2.5,0) coordinate(vin2-)
    % segunda etapa
                    node[op amp, anchor=-] (opamp2) {}
                    (opamp2.up) ++ (.2,0) node[right=2pt] {U2}
                    (opamp2.down) ++ (.2,0) node[below=2pt, right=2pt] {OPA2134}
                    (opamp2.up) to[C, l=$C_{2}$, a=\SI{100}{\nano\farad}] ++(0,1.2) node[vcc](vcc) {} node[above right=.5pt] {+9~V}
                    (opamp2.down) -- node[ground, scale=2] {} ++(0,0)
                    (opamp2.down) node[below=1pt, right] {$-$}
                    (opamp2.up) node[above=2pt, right=-0.5pt] {$+$}

                    (opamp2.+) -- ++(0,-1) coordinate(VD2)
                    to[R] node[above=35pt, right=4pt] {$R_{7}$} node[above=25pt,
                    right=4pt] {\SI{10}{\kilo\ohm}} (VD2 |- d4gnd) node[ground, scale=2] {} 
                    (VD2) to[short,*-] ++(.75,0)
                    to[R, l=$R_{6}$, a=\SI{10}{\kilo\ohm}] ++(.75,0) to[short,-*] ++(.75,0) node[right] {+9 $\mathrm{V}$} % Resistencia del segundo divisor
                    (VD2) ++(0,-.5) to[short, *-] ++(-1.15,0) coordinate(cR7)
                    to[C] node[above=5.5ex, right=1ex] {$C_{6}$} node[above=3ex, right=.5ex] {\SI{100}{\nano\farad}} (cR7 |- d4gnd) node[ground, scale=2] {}

                    (vin2-) ++(-.5,0) coordinate(vin2-_new)
                    to[short, *-] (vin2-_new |- r3_out1)
                    to[R, l=$R_{5}$, a=\SI{100}{\kilo\ohm}] ++(4.5,0) coordinate(r5_out1)
                    (opamp2.out) -- (r5_out1 |- opamp2.out) coordinate(vout2_node1)
                    to[short,*-] (vout2_node1 |- r5_out1)
    % out, final del circuito
                    (vout2_node1) to[short, *-o] ++(1,0) node[above] {Output}
                    (r3_out1) to[short, *-] ++(0,1.5) to[C, l=$C_{1}$, a=\SI{5}{\pico\farad}] ++(-4.5,0)
                    to[short, -*] ++(0,-1.5)
                    (r5_out1) to[short, *-] ++(0,1.5) to[C, l^=$C_{5}$, a=\SI{10}{\pico\farad}] ++(-4.5,0)
                    to[short, -*] ++(0,-1.5)
                    ;
                \end{circuitikz}
%                \includegraphics[width=\linewidth]{circuito.pdf}
                \caption{Circuito completo}
                \label{fig:circ}
            \end{figure}

            \begin{figure}[!t]
                \centering
                \subfloat[] {%
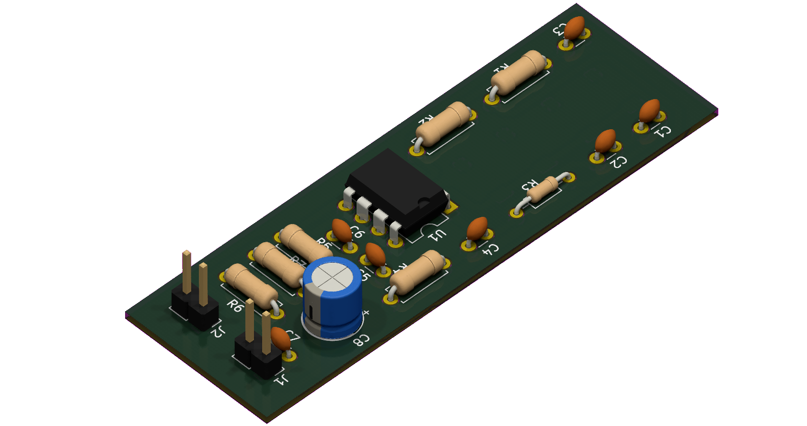
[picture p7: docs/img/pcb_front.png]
                    
                    \label{subfig:pcb_front}
                }
                \hfil
                \subfloat[] {%
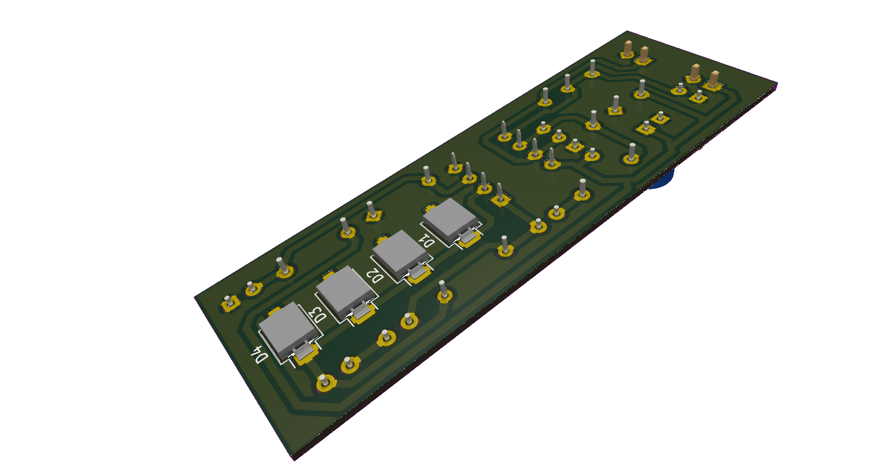
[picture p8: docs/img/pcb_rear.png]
                    
                    \label{subfig:pcb_rear}
                }
                \caption{Modelado 3D del PCB. (a) Parte frontal, (b) parte
                posterior}
                \label{fig:pcb}
            \end{figure}

\section{Limitaciones del Diseño}
    Las limitaciones o posibles mejoras del diseño actual son las siguientes
    \begin{enumerate}
        \item Niveles de energía cinética detectables: Como se ha expresado
            anteriormente, el nivel máximo de energía medible es 60 KeV, lo cúal
            es un valor relativamente bajo para partículas $\beta-$; partículas
            con más energía no serán medidas correctamente. Esto es debido
            principalmente al área efectiva de detección (área física de la zona
            sensible de los diodos) y al valor de capacitancia del diodo para
            $\mathrm{V_{R}}$ dado. Una mejora viable para este problema es el
            aumento del voltaje de alimentación, de manera tal que aumente
            $\mathrm{V_{R}}$.

        \item Nivel de ruido: el capacitor C4 que se puede observar en la
            Fig.~\ref{fig:circ} tiene un papel fundamental en los niveles de
            ruido de la salida del circuito. Empíricamente se pudo advertir
            que utilizando un valor de 22 pF en lugar de 5 pF, las mediciones  
            de los picos fueron más limpias.
    \end{enumerate}

\section{Conclusiones}
    Aunque el diseño de detectores de partículas con fotodiodos requiere de un nivel de
    precisión muy grande para evitar capacitancias parásitas y obtener el menor
    nivel de ruido posible montado en la señal de salida, es posible realizar
    mediciones de radiación $\beta-$ utilizando un amplificador operacional
    basado en JFET en configuración transimpedancia. 
% Las malditas referencias. TODO: Sacar este comment.
\bibliographystyle{IEEEtran}
\bibliography{refs}
\nocite{*}
\end{document}

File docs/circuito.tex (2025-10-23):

\documentclass[11pt]{article}
\usepackage{circuitikz}

\begin{document}
\ctikzset{bipoles/length=7mm, amp symbol font={\scriptsize}}
\begin{circuitikz}[american, font=\scriptsize, transform shape, scale=0.75]
    %\ctikzset{diodes/scale=0.5}
    \centering
    \draw
    (0,0) to[photodiode,name=D1] (0,5)
    node[above left=3pt](D1label) at (D1) {$D_{1}$}
    node[below left=3pt] at (D1) {BPW34S}
    (0,0) node[ground, scale=1.4] {}

    (2,0) to[photodiode,name=D2] (2,5)
    node[above left=3pt] at (D2) {$D_{2}$}
    node[below left=3pt] at (D2) {BPW34S}
    (2,0) node[ground, scale=1.4] {}

    (4,0) to[photodiode,name=D3] (4,5)
    node[above left=3pt] at (D3) {$D_{3}$}
    node[below left=3pt] at (D3) {BPW34S}
    (4,0) node[ground, scale=1.4] {}

    (6,0) to[photodiode,name=D4] (6,5) coordinate(vd4)
    node[above left=3pt] at (D4) {$D_{4}$}
    node[below left=3pt] at (D4) {BPW34S}
    (6,0) node[ground, scale=1.4](d4gnd) {}

    % muevo el cursor desde gnd de D4 hasta donde termina la pata de D4 creo una linea desde el D4 con long = 1
    ++(0,5)
    to[short] ++(2,0)

    node[op amp, anchor=-] (opamp) {}
    (0,5) -- (opamp.-)
    (opamp.up) ++ (.2,0) node[right=2pt] {U1}
    (opamp.down) ++ (.2,0) node[below=2pt, right=2pt] {OPA2134}
    (opamp.down) -- node[ground, scale=1.4] {} ++(0,0)
    (opamp.down) node[below=1pt, right] {$-$}
    (opamp.up) node[above=2pt, right=-0.5pt] {$+$}
    (opamp.+) -- ++(0,-1) coordinate(VD1)
    % primer divisor
    to[R, l=$R_{2}$] (VD1 |- d4gnd) node[ground, scale=1.4] {}
    (VD1) to[short,*-] ++(.75,0)
    to[R, l=$R_{1}$] ++(.75,0) to[short,-*] ++(.75,0) node[right] {+9 $\mathrm{V}$} % Resistencia del divisor
    (opamp.up) %-- ++(0,.5) coordinate(V+C1)
    to[C, l=$C_{5}$] ++(0,1.2) node[vcc](vcc) {} node[above right=.5pt] {+9~V}
    (vd4) to[short, *-] ++(0,2)
    to[R, l=$R_{3}$, a=10 M$\Omega$] ++(4.5,0) coordinate(r3_out1)
    (opamp.out) -- (r3_out1 |- opamp.out) coordinate(vout1_node1)
    % capacitor en paralelo a R3
    %(r3_out1) to[short, *-] ++(0,1)
    to[short,*-] (vout1_node1 |- r3_out1)
    (vout1_node1 |- vout1_node1) to[C, l=$C_{4}$] ++(1.5,0)
    to[R, l=$R_{4}$] ++(2.5,0) coordinate(vin2-)
    % segunda etapa
    node[op amp, anchor=-] (opamp2) {}
    (opamp2.up) ++ (.2,0) node[right] {U2}
    (opamp2.down) ++ (.2,0) node[right] {OPA2134}
    (opamp2.up) to[C, l=$C_{5}$] ++(0,1.2) node[vcc](vcc) {} node[above right=.5pt] {+9~V}
    (opamp2.down) -- node[ground, scale=1.4] {} ++(0,0)
    (opamp2.down) node[right] {-}
    
    (opamp2.+) -- ++(0,-1) coordinate(VD2)
    to[R] (VD2 |- d4gnd) node[above right] {R7} node[ground, scale=1.4] {} 
    (VD2) to[short,*-] ++(.75,0)
    to[R, l=$R_{6}$, a=10 K$\Omega$] ++(.75,0) to[short,-*] ++(.75,0) node[right] {+9 $\mathrm{V}$} % Resistencia del segundo divisor
    (VD2) ++(0,-.5) to[short, *-] ++(-1.15,0) coordinate(cr7)
    to[C, l=$C_{7}$] (cr7 |- d4gnd) node[ground, scale=1.4] {}

    (vin2-) ++(-.5,0) coordinate(vin2-_new)
    to[short, *-] (vin2-_new |- r3_out1)
    to[R, l=$R_{5}$] ++(4.5,0) coordinate(r5_out1)
    (opamp2.out) -- (r5_out1 |- opamp2.out) coordinate(vout2_node1)
    to[short,*-] (vout2_node1 |- r5_out1)
    % out, final del circuito
    (vout2_node1) to[short, *-o] ++(1,0) node[above] {Output}
    (r3_out1) to[short, *-] ++(0,1.5) to[C, l^=$C_{1}$] ++(-4.5,0)
    to[short, -*] ++(0,-1.5)
    (r5_out1) to[short, *-] ++(0,1.5) to[C, l^=$C_{6}$] ++(-4.5,0)
    to[short, -*] ++(0,-1.5)
    ;
\end{circuitikz}
\end{document}

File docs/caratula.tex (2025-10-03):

\begin{titlepage}
    \begin{center}
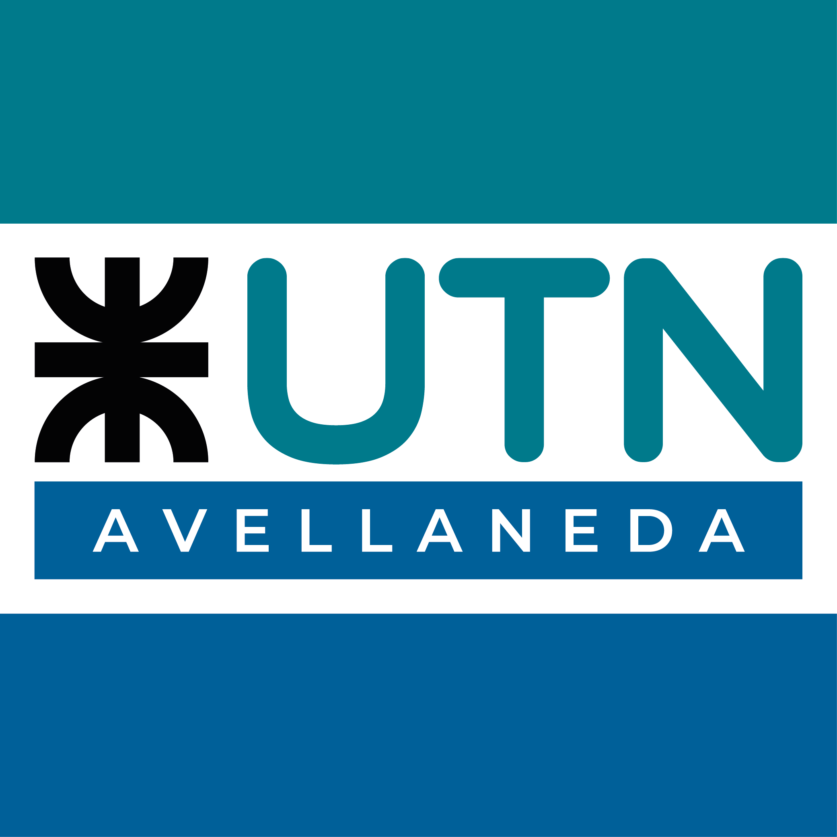
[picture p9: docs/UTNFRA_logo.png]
        
    \end{center}
\end{titlepage}

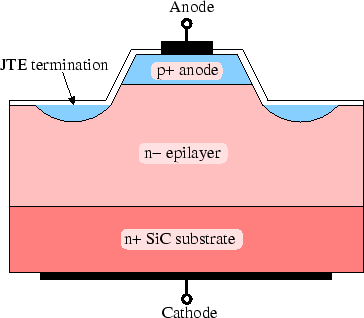
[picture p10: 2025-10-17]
docs/img/another_pin.png

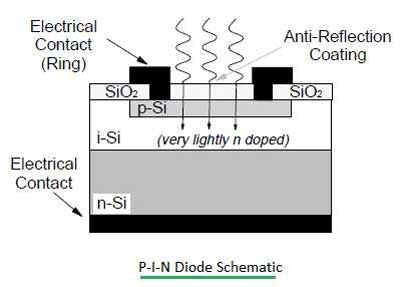
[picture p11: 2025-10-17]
docs/img/PIN_structure.jpg

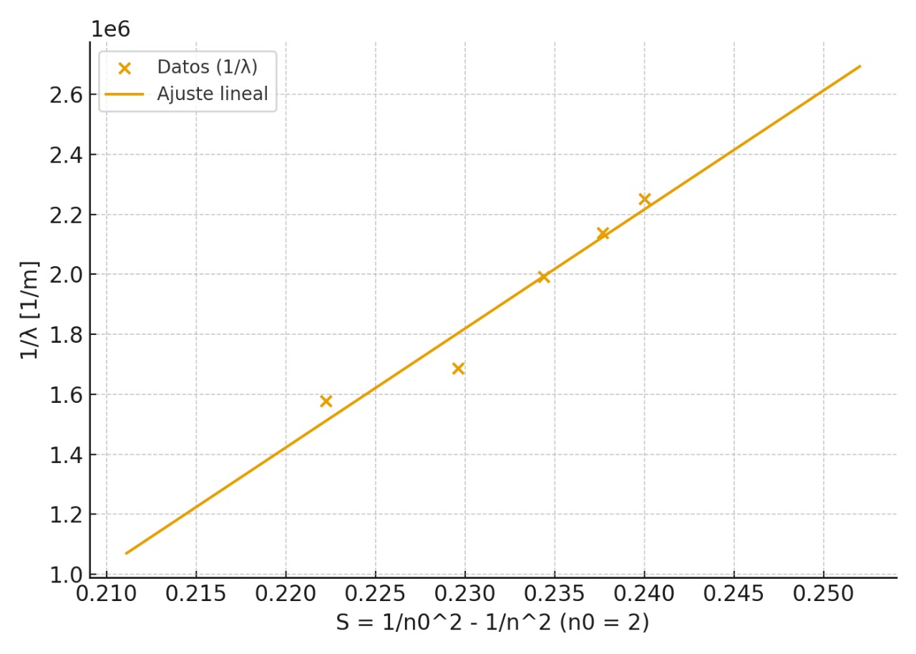
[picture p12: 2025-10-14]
KiCAD/2d39423e-f3e0-42a1-b1c0-b04ef338b473.jpeg

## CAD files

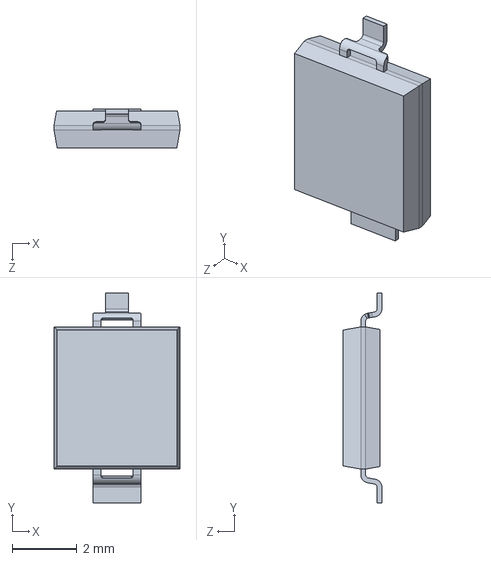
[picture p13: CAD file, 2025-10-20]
KiCAD/3D/BPW_34_S_20180209_geometry.STEP
3.90 x 6.50 x 1.20 mm

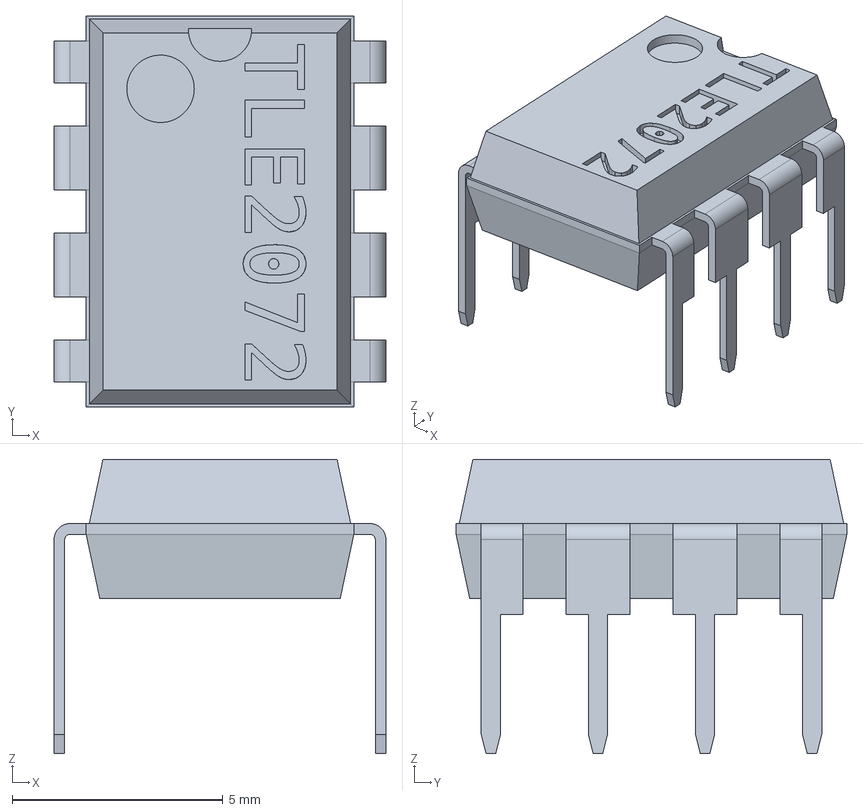
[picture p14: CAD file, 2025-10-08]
KiCAD/3D/TLE2072.step
7.87 x 9.27 x 6.98 mm

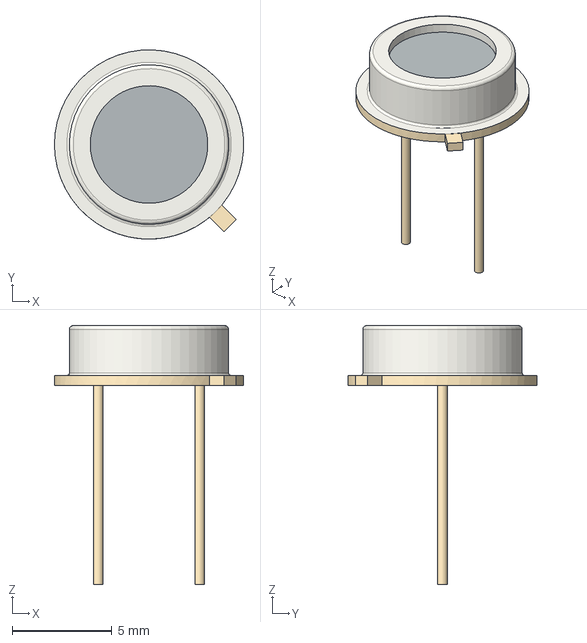
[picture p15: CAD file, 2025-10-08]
KiCAD/3D/BPX61.step
9.49 x 9.50 x 13.0 mm

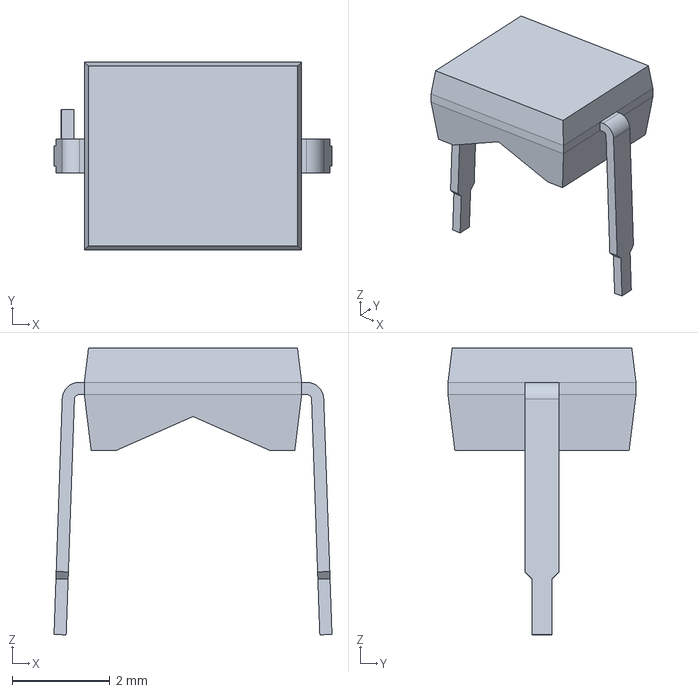
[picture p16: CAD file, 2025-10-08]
KiCAD/3D/BPW34.FCStd
5.69 x 3.85 x 5.87 mm

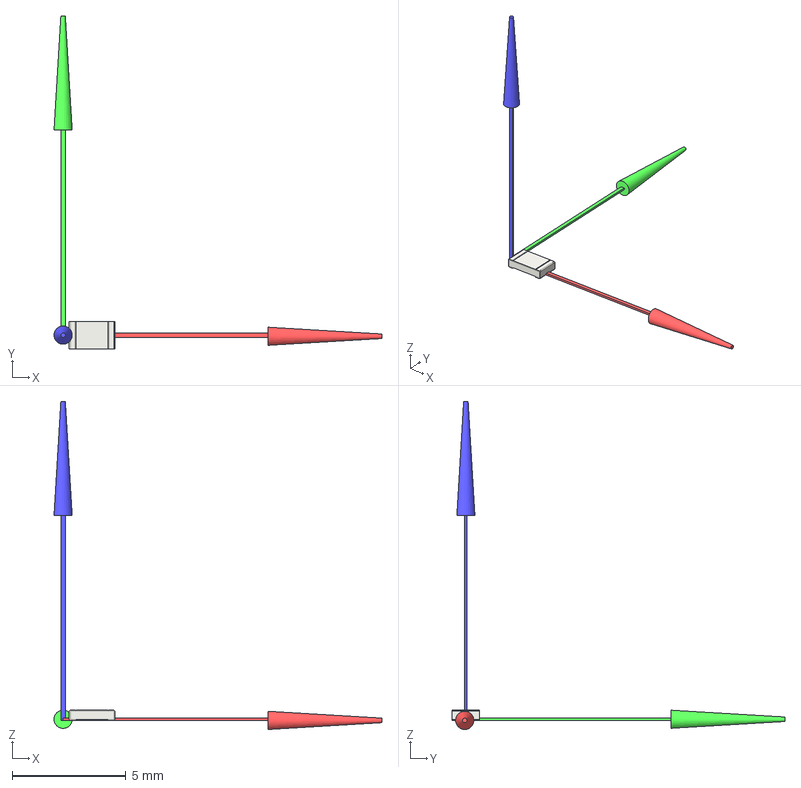
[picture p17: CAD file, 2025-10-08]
KiCAD/3D/R_0805_2012Metric_THTorigin.FCStd
14.4 x 14.6 x 14.4 mm
R_0805_2012Metric_THTorigin
Z
Y
X

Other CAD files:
KiCAD/3D/BPW34F.step
KiCAD/3D/TLE2072ACP.FCStd
KiCAD/3D/BPX61.FCStd

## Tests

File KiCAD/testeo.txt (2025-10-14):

######### Sin el opamp conectado #########

AMP_A (entrada):
    Vout = 0.57 V
    Vin- = 0.84 V
    Vin+ = 6.67 V (Tensión del divisor entre R2 y R1)

AMP_B (salida):
    Vout = 0 V
    Vin- = 0 V
    Vin+ = 4.38 V (Tensión del divisor entre R6 y R7)

######### Chequeo de pistas (continuidad) #########

- Diodos -> OK, están en inversa.
- Tengo las tensiones bien en los divisores, por lo tanto las R1, R2, R6, R7 y
  sus respectivas pistas están bien. 
- Todas las pistas estan bien.
- 
- 
-

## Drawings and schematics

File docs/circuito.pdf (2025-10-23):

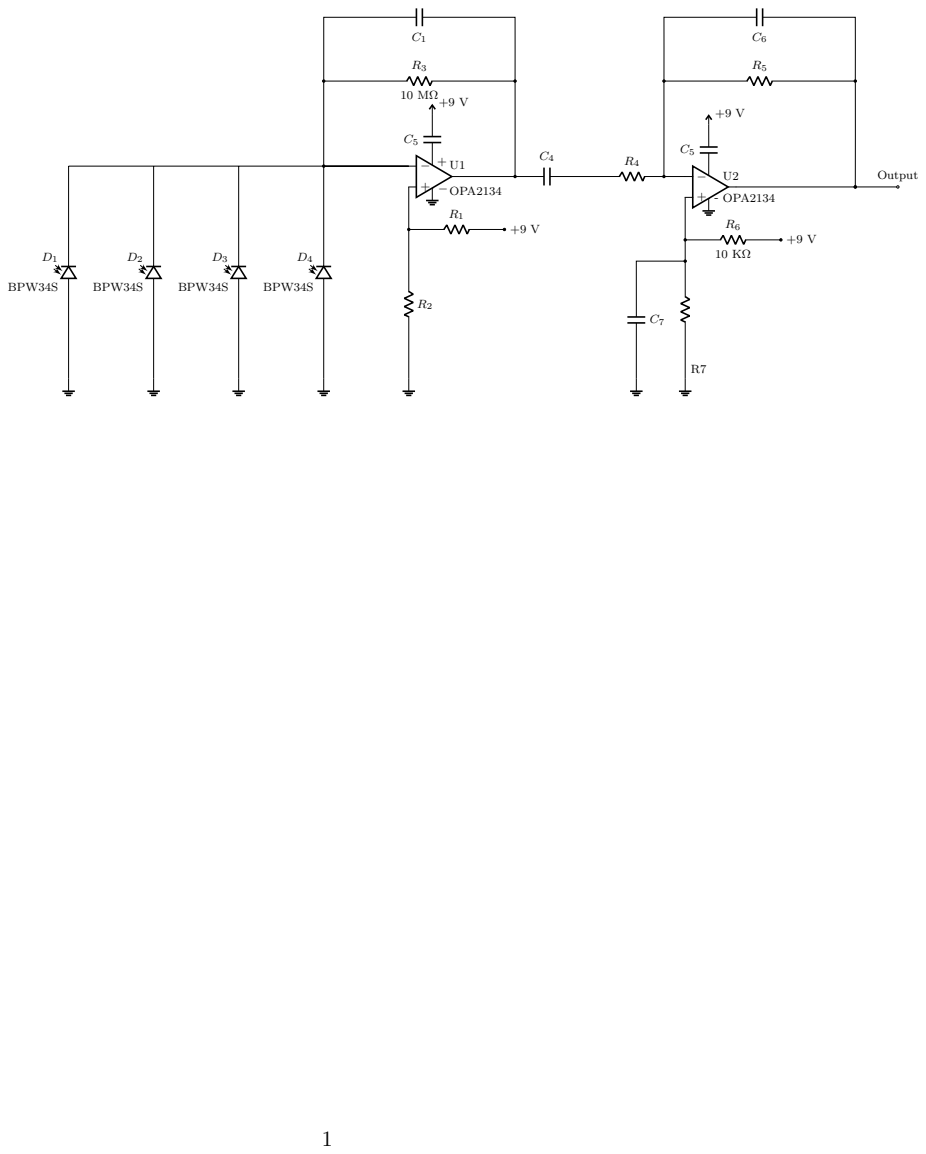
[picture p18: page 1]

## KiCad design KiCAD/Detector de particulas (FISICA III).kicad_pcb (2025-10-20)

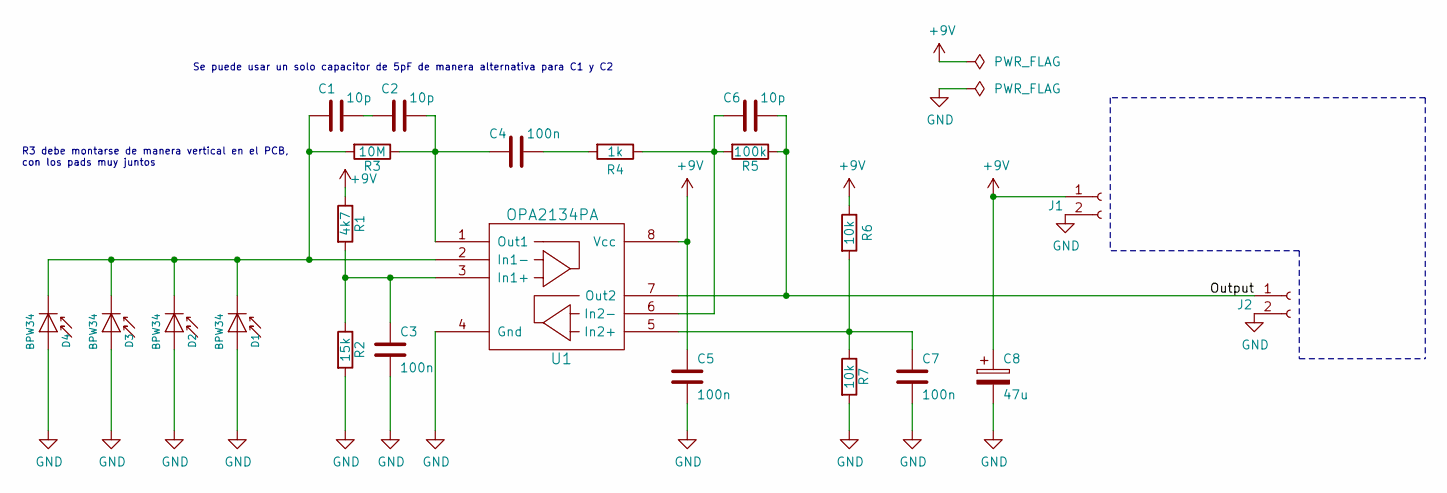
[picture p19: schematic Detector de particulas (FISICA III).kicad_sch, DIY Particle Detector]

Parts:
C1, C2: 10p; C_Disc_D3.0mm_W1.6mm_P2.50mm; MFG_PN MC0805N100J101A2.54MM; FARNELL 1694175
C3, C5, C7: 100n; C_Disc_D3.0mm_W1.6mm_P2.50mm; MFG_PN MC0805Y104M500A2.54MM; FARNELL 2112751
C4: 100n; C_Disc_D3.0mm_W1.6mm_P2.50mm; MFG_PN C320C474M5U5TA; FARNELL 1457660
C6: 10p; C_Disc_D3.0mm_W1.6mm_P2.50mm; MFG_PN TS170R1H332KSBBA0R; FARNELL 2901293
C8: 47u; CP_Radial_D6.3mm_P2.50mm; MFG_PN ECA-1JHG470; FARNELL 9693033
D1, D2, D3: BPW34; Osram_BPW34S-SMD; MFG_PN BPW34F/FA; FARNELL 2981621
D4: BPW34; Osram_BPW34S-SMD; MFG_PN BPX61; FARNELL 2981630
J1, J2: Conn_01x02_Female; PinHeader_1x02_P2.54mm_Vertical
R1: 4k7; R_Axial_DIN0207_L6.3mm_D2.5mm_P7.62mm_Horizontal; MFG_PN MCMF006FF4701A50; FARNELL 2401772
R2: 15k; R_Axial_DIN0207_L6.3mm_D2.5mm_P7.62mm_Horizontal; MFG_PN MCMF006FF1502A50; FARNELL 2401785
R3: 10M; R_Axial_DIN0204_L3.6mm_D1.6mm_P7.62mm_Horizontal; MFG_PN RH73H2A40MKTN; FARNELL 1174521
R4: 1k; R_Axial_DIN0207_L6.3mm_D2.5mm_P7.62mm_Horizontal; MFG_PN MCMF006FF4701A50; FARNELL 2401772
R5: 100k; R_Axial_DIN0207_L6.3mm_D2.5mm_P7.62mm_Horizontal; MFG_PN MCMF006FF1004A50; FARNELL 2401807
R6, R7: 10k; R_Axial_DIN0207_L6.3mm_D2.5mm_P7.62mm_Horizontal; MFG_PN MCMF006FF1002A50; FARNELL 2401780
U1: OPA2134PA; DIP-8_W7.62mm; FARNELL 3117956

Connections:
+9V: C5.1, C8.1, J1.1, R1.1, R6.1, U1.8 (Vcc)
/Output: C6.2, J2.1, R5.1, U1.7 (Out2)
GND: C3.2, C5.2, C7.2, C8.2, D1.2 (A), D2.2 (A), D3.2 (A), D4.2 (A), J1.2, J2.2, R2.2, R7.2, U1.4 (Gnd)
unnamed: C1.2, C2.1
unnamed: C4.2, R4.2
unnamed: C1.1, D1.1 (K), D2.1 (K), D3.1 (K), D4.1 (K), R3.2, U1.2 (In1-)
unnamed: C3.1, R1.2, R2.1, U1.3 (In1+)
unnamed: C7.1, R6.2, R7.1, U1.5 (In2+)
unnamed: C6.1, R4.1, R5.2, U1.6 (In2-)
unnamed: C2.2, C4.1, R3.1, U1.1 (Out1)

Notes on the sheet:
Se puede usar un solo capacitor de 5pF de manera alternativa para C1 y C2
R3 debe montarse de manera vertical en el PCB, con los pads muy juntos

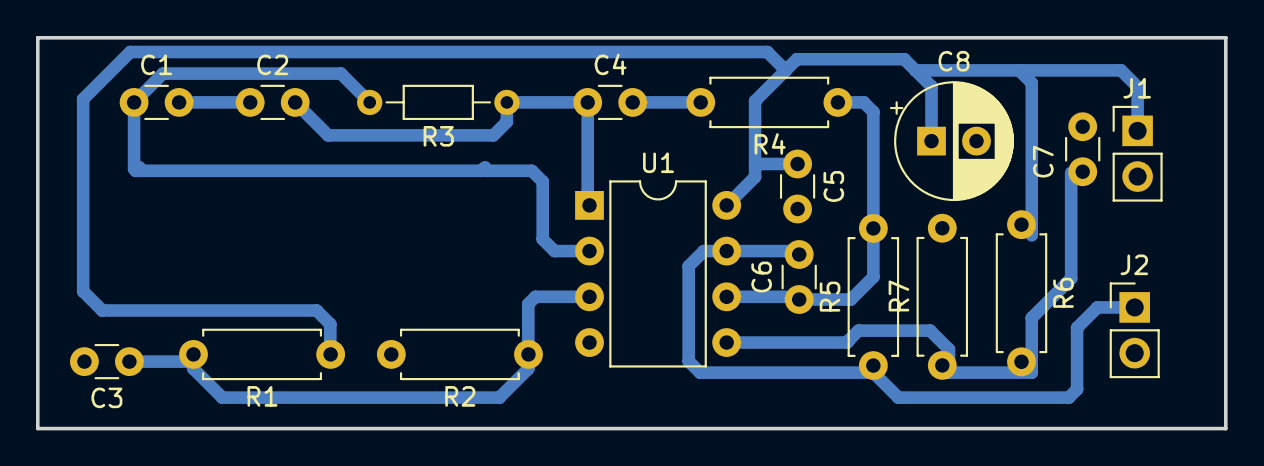
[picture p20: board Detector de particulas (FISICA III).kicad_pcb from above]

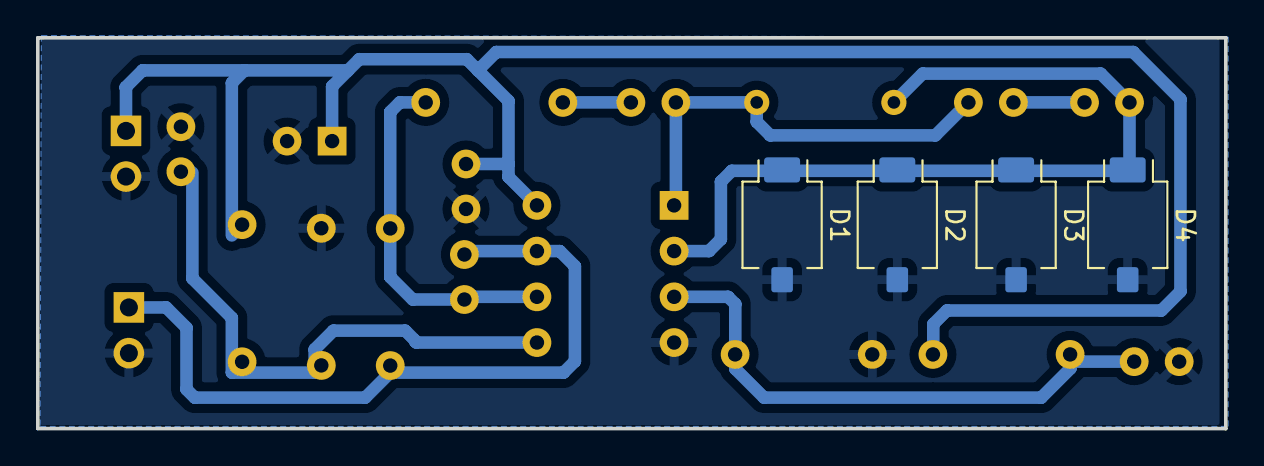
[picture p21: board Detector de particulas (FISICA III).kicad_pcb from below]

Board: 2 copper layers, 66.0 x 21.7 mm, 22 parts (4 on the bottom side), 10 nets.

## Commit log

2025-10-07 ya esta el template de referencias. Avances
2025-10-08 ppio de funcionamiento avanzado
2025-10-08 repo actualizado
    [1-click-bom_alpha-spectrometer.csv, 1-click-bom_electron-detector.csv, BPW34.FCStd, BPW34F.step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]
2025-10-14 bastante documentacion y algunos testeos
    [OPAx134_Test_Circuit.DSN]
2025-10-15 un poco de limpieza del repo
    [1-click-bom_alpha-spectrometer.csv, 1-click-bom_electron-detector.csv, BPW34.FCStd, BPW34F.step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]
2025-10-16 nuevo pcb
    [Detector de particulas (FISICA III).kicad_pcb, Detector de particulas (FISICA III).kicad_sch]
2025-10-16 nuevo pcb completo
    [Detector de particulas (FISICA III).kicad_pcb]
2025-10-20 etapa de deteccion completa
2025-10-20 primera version terminada
    [BPW_34_S_20180209_geometry.STEP, Detector de particulas (FISICA III).kicad_pcb, Detector de particulas (FISICA III).kicad_sch]
2025-10-20 informe v2
    [Detector de particulas (FISICA III).kicad_pcb]
2025-10-23 circuito en circuitikz terminado

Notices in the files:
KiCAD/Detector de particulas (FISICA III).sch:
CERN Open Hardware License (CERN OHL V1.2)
